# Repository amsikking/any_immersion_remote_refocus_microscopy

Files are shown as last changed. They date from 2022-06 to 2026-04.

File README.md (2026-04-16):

# Any immersion remote refocus (AIRR) microscopy



A scientific publication that describes a new approach for any immersion remote refocus (AIRR) microscopy. This repository 
hosts everything you need to reproduce our results. Read the publication here:
https://amsikking.github.io/any_immersion_remote_refocus_microscopy (hosted via Alfred Millett-Sikking's personal GitHub account).

This repository is intended to hold a (mostly) self-contained scientific publication. It contains:

* HTML, javascript, CSS, and small images (`index.html`, `appendix.html`, and the `javascript`, `stylesheets`, and `images` directories)
* A (limited) PDF version of the publication; note that this does not include animated/interactive figures.
* Code which produces figures (in the `figures` directory). You can run and modify this code to verify and explore our results.

<a rel="license" href="http://creativecommons.org/licenses/by/4.0/">
  </a>
  <br />This work is licensed under a 
  <a rel="license" href="http://creativecommons.org/licenses/by/4.0/">Creative Commons Attribution 4.0 International License</a>.

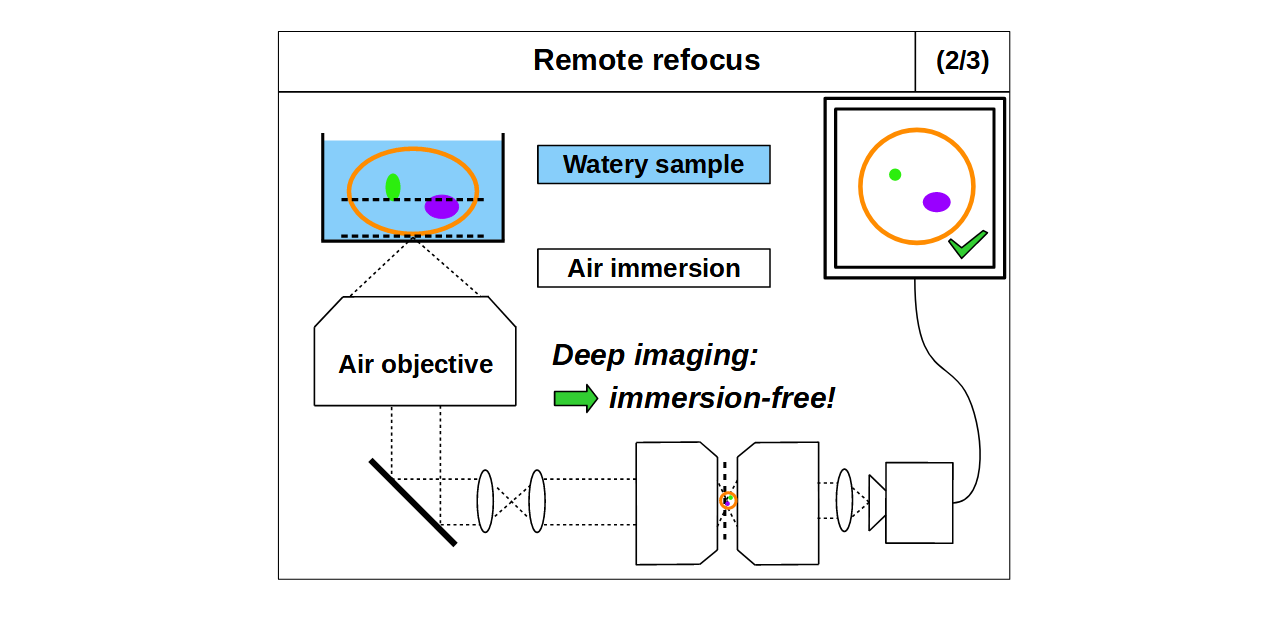
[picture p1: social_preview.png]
social_preivew


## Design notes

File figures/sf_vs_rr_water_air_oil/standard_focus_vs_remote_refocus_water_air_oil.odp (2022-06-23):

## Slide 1

Standard focus

(1/3)

Watery sample

Water immersion

Deep imaging:

needs matched refractive index

Water objective

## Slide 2

Standard focus

(1/3)

Watery sample

Water immersion

Deep imaging:

needs matched refractive index

Water objective

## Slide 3

Standard focus

(1/3)

Watery sample

Water immersion

Deep imaging:

needs matched refractive index

Water objective

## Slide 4

Standard focus

(1/3)

Watery sample

Water immersion

Water objective

Deep imaging:

needs matched refractive index

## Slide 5

Standard focus

(1/3)

Watery sample

Watery sample

Water immersion

Water immersion

Water objective

Deep imaging:

needs matched refractive index

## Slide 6

Standard focus

(1/3)

Watery sample

Water immersion

Water objective

Deep imaging:

needs matched refractive index

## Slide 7

Standard focus

(1/3)

Watery sample

Water immersion

Water objective

Deep imaging:

needs matched refractive index

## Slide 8

Standard focus

(1/3)

Watery sample

Water immersion

Water objective

Deep imaging:

needs matched refractive index

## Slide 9

Standard focus

(1/3)

Watery sample

Water immersion

Water objective

Deep imaging:

needs matched refractive index

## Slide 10

Standard focus

(1/3)

Watery sample

Water immersion

Water objective

Deep imaging:

needs matched refractive index

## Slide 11

Standard focus

(1/3)

Watery sample

Water immersion

Water objective

Deep imaging:

needs matched refractive index

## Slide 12

Standard focus

(1/3)

Watery sample

Water immersion

Water objective

Deep imaging:

needs matched refractive index

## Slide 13

Standard focus

(1/3)

Watery sample

Water immersion

Deep imaging:

needs matched refractive index

Water objective

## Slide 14

Standard focus

(1/3)

Watery sample

Water immersion

Deep imaging:

needs matched refractive index

Water objective

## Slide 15

Standard focus

(1/3)

Watery sample

Water immersion

Deep imaging:

needs matched refractive index

Water objective

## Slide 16

Standard focus

(2/3)

Watery sample

Air immersion

Deep imaging:

disrupted by spherical aberration

Air objective

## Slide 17

Standard focus

(2/3)

Watery sample

Air immersion

Deep imaging:

disrupted by spherical aberration

Air objective

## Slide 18

Standard focus

(2/3)

Watery sample

Air immersion

Deep imaging:

disrupted by spherical aberration

Air objective

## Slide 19

Standard focus

(2/3)

Watery sample

Air immersion

Air objective

Deep imaging:

disrupted by spherical aberration

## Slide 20

Standard focus

(2/3)

Watery sample

Air immersion

Air objective

Deep imaging:

disrupted by spherical aberration

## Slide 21

Standard focus

(2/3)

Watery sample

Air immersion

Air objective

Deep imaging:

disrupted by spherical aberration

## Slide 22

Standard focus

(2/3)

Watery sample

Air immersion

Air objective

Deep imaging:

disrupted by spherical aberration

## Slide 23

Standard focus

(2/3)

Watery sample

Air immersion

Air objective

Deep imaging:

disrupted by spherical aberration

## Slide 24

Standard focus

(2/3)

Watery sample

Air immersion

Air objective

Deep imaging:

disrupted by spherical aberration

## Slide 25

Standard focus

(2/3)

Watery sample

Air immersion

Air objective

Deep imaging:

disrupted by spherical aberration

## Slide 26

Standard focus

(2/3)

Watery sample

Air immersion

Air objective

Deep imaging:

disrupted by spherical aberration

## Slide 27

Standard focus

(2/3)

Watery sample

Air immersion

Air objective

Deep imaging:

disrupted by spherical aberration

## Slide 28

Standard focus

(2/3)

Watery sample

Air immersion

Deep imaging:

disrupted by spherical aberration

Air objective

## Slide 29

Standard focus

(2/3)

Watery sample

Air immersion

Deep imaging:

disrupted by spherical aberration

Air objective

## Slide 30

Standard focus

(2/3)

Watery sample

Air immersion

Deep imaging:

disrupted by spherical aberration

Air objective

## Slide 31

Standard focus

(3/3)

Watery sample

Oil immersion

Deep imaging:

disrupted by spherical aberration

Oil objective

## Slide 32

Standard focus

(3/3)

Watery sample

Oil immersion

Deep imaging:

disrupted by spherical aberration

Oil objective

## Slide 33

Standard focus

(3/3)

Watery sample

Oil immersion

Deep imaging:

disrupted by spherical aberration

Oil objective

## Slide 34

Standard focus

(3/3)

Watery sample

Oil immersion

Oil objective

Deep imaging:

disrupted by spherical aberration

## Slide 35

Standard focus

(3/3)

Watery sample

Oil immersion

Oil objective

Deep imaging:

disrupted by spherical aberration

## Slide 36

Standard focus

(3/3)

Watery sample

Oil immersion

Oil objective

Deep imaging:

disrupted by spherical aberration

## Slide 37

Standard focus

(3/3)

Watery sample

Oil immersion

Oil objective

Deep imaging:

disrupted by spherical aberration

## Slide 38

Standard focus

(3/3)

Watery sample

Oil immersion

Oil objective

Deep imaging:

disrupted by spherical aberration

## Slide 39

Standard focus

(3/3)

Watery sample

Oil immersion

Oil objective

Deep imaging:

disrupted by spherical aberration

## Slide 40

Standard focus

(3/3)

Watery sample

Oil immersion

Oil objective

Deep imaging:

disrupted by spherical aberration

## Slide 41

Standard focus

(3/3)

Watery sample

Oil immersion

Oil objective

Deep imaging:

disrupted by spherical aberration

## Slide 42

Standard focus

(3/3)

Watery sample

Oil immersion

Oil objective

Deep imaging:

disrupted by spherical aberration

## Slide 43

Standard focus

(3/3)

Watery sample

Oil immersion

Deep imaging:

disrupted by spherical aberration

Oil objective

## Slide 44

Standard focus

(3/3)

Watery sample

Oil immersion

Deep imaging:

disrupted by spherical aberration

Oil objective

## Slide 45

Standard focus

(3/3)

Watery sample

Oil immersion

Deep imaging:

disrupted by spherical aberration

Oil objective

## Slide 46

Remote refocus

(1/3)

Watery sample

Water immersion

Deep imaging:

extra range!

Water objective

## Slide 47

Remote refocus

(1/3)

Watery sample

Water immersion

Deep imaging:

extra range!

Water objective

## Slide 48

Remote refocus

(1/3)

Watery sample

Water immersion

Deep imaging:

extra range!

Water objective

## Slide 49

Remote refocus

(1/3)

Watery sample

Water immersion

Deep imaging:

extra range!

Water objective

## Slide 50

Remote refocus

(1/3)

Watery sample

Water immersion

Deep imaging:

extra range!

Water objective

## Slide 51

Remote refocus

(1/3)

Watery sample

Water immersion

Deep imaging:

extra range!

Water objective

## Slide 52

Remote refocus

(1/3)

Watery sample

Water immersion

Deep imaging:

extra range!

Water objective

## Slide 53

Remote refocus

(1/3)

Watery sample

Water immersion

Deep imaging:

extra range!

Water objective

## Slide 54

Remote refocus

(1/3)

Watery sample

Water immersion

Deep imaging:

extra range!

Water objective

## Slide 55

Remote refocus

(1/3)

Watery sample

Water immersion

Deep imaging:

extra range!

Water objective

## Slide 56

Remote refocus

(1/3)

Watery sample

Water immersion

Deep imaging:

extra range!

Water objective

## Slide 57

Remote refocus

(1/3)

Watery sample

Water immersion

Deep imaging:

extra range!

Water objective

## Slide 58

Remote refocus

(1/3)

Watery sample

Water immersion

Deep imaging:

extra range!

Water objective

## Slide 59

Remote refocus

(1/3)

Watery sample

Water immersion

Deep imaging:

extra range!

Water objective

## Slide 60

Remote refocus

(1/3)

Watery sample

Water immersion

Deep imaging:

extra range!

Water objective

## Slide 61

Remote refocus

(2/3)

Watery sample

Air immersion

Deep imaging:

immersion-free!

Air objective

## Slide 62

Remote refocus

(2/3)

Watery sample

Air immersion

Deep imaging:

immersion-free!

Air objective

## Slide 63

Remote refocus

(2/3)

Watery sample

Air immersion

Deep imaging:

immersion-free!

Air objective

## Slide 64

Remote refocus

(2/3)

Watery sample

Air immersion

Deep imaging:

immersion-free!

Air objective

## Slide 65

Remote refocus

(2/3)

Watery sample

Air immersion

Deep imaging:

immersion-free!

Air objective

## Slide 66

Remote refocus

(2/3)

Watery sample

Air immersion

Deep imaging:

immersion-free!

Air objective

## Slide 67

Remote refocus

(2/3)

Watery sample

Air immersion

Deep imaging:

immersion-free!

Air objective

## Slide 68

Remote refocus

(2/3)

Watery sample

Air immersion

Deep imaging:

immersion-free!

Air objective

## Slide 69

Remote refocus

(2/3)

Watery sample

Air immersion

Deep imaging:

immersion-free!

Air objective

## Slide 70

Remote refocus

(2/3)

Watery sample

Air immersion

Deep imaging:

immersion-free!

Air objective

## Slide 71

Remote refocus

(2/3)

Watery sample

Air immersion

Deep imaging:

immersion-free!

Air objective

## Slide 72

Remote refocus

(2/3)

Watery sample

Air immersion

Deep imaging:

immersion-free!

Air objective

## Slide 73

Remote refocus

(2/3)

Watery sample

Air immersion

Deep imaging:

immersion-free!

Air objective

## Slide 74

Remote refocus

(2/3)

Watery sample

Air immersion

Deep imaging:

immersion-free!

Air objective

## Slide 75

Remote refocus

(2/3)

Watery sample

Air immersion

Deep imaging:

immersion-free!

Air objective

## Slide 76

Remote refocus

(3/3)

Watery sample

Oil immersion

Deep imaging:

highest NA!

Oil objective

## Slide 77

Remote refocus

(3/3)

Watery sample

Oil immersion

Deep imaging:

highest NA!

Oil objective

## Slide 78

Remote refocus

(3/3)

Watery sample

Oil immersion

Deep imaging:

highest NA!

Oil objective

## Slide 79

Remote refocus

(3/3)

Watery sample

Oil immersion

Deep imaging:

highest NA!

Oil objective

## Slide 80

Remote refocus

(3/3)

Watery sample

Oil immersion

Deep imaging:

highest NA!

Oil objective

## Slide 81

Remote refocus

(3/3)

Watery sample

Oil immersion

Deep imaging:

highest NA!

Oil objective

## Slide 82

Remote refocus

(3/3)

Watery sample

Oil immersion

Deep imaging:

highest NA!

Oil objective

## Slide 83

Remote refocus

(3/3)

Watery sample

Oil immersion

Deep imaging:

highest NA!

Oil objective

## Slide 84

Remote refocus

(3/3)

Watery sample

Oil immersion

Deep imaging:

highest NA!

Oil objective

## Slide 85

Remote refocus

(3/3)

Watery sample

Oil immersion

Deep imaging:

highest NA!

Oil objective

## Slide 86

Remote refocus

(3/3)

Watery sample

Oil immersion

Deep imaging:

highest NA!

Oil objective

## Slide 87

Remote refocus

(3/3)

Watery sample

Oil immersion

Deep imaging:

highest NA!

Oil objective

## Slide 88

Remote refocus

(3/3)

Watery sample

Oil immersion

Deep imaging:

highest NA!

Oil objective

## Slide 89

Remote refocus

(3/3)

Watery sample

Oil immersion

Deep imaging:

highest NA!

Oil objective

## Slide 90

Remote refocus

(3/3)

Watery sample

Oil immersion

Deep imaging:

highest NA!

Oil objective

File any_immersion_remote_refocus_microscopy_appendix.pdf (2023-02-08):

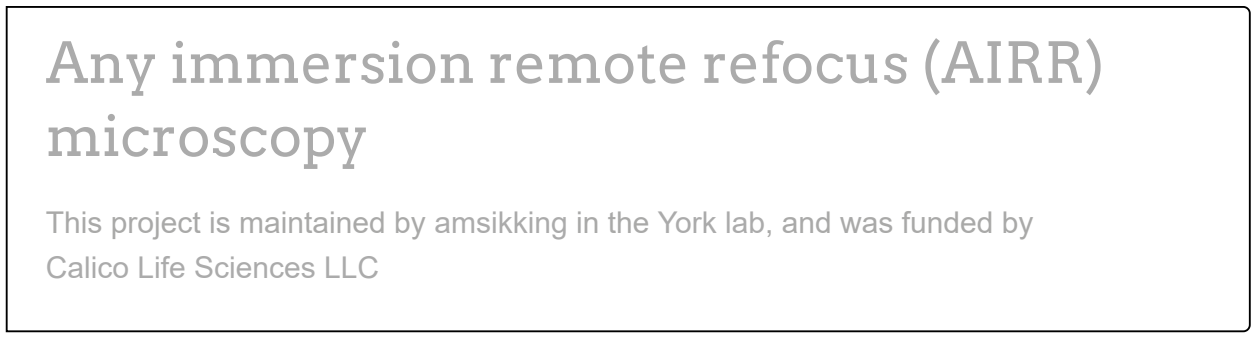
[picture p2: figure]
Any immersion remote refocus (AIRR) microscopy; Calico Life Sciences LLC

This project is maintained by amsikking (https://amsikking.github.io/) in the York lab, (https://andrewgyork.github.io/) and was funded by

# Appendix

Note that this is a limited PDF or print version; animated and interactive figures are disabled. For the full version of this article, please visit one of the following links: https://amsikking.github.io/any_immersion_remote_refocus_microscop y (https://amsikking.github.io/any_immersion_remote_refocus_microscopy)

# Any immersion remote refocus (AIRR) microscopy

Back to the main text

## Theory

Here we present the equations used in the main article.

Numerical aperture and resolution

The numerical aperture (NA) is defined as:

where | is the refractive index (RI) of the immersion medium and | is the collection half-angle of the objective.
In the case of a planar RI boundary like a coverslip the NA is conserved via Snell's law:
where | is the RI of the sample and | is the collection half-angle in sample space. According to the Rayleigh
criteria the smallest resolvable feature size | is then:
NA = ni sin θi | (a1)
ni | θi
ns sin θs = ni sin θi | (a2)
ns | θs

rmin where is the wavelength of the collected light [Pawley 2006]. (https://doi.org/10.1007/978-0-387-45524-2)

Focal length, field of view and pixels

The objective lens focal length is found with:

where | is the tube lens focal length (200mm for Nikon) and | is the magnification of the objective. The
sample space field of view (FOV) is then assumed to be:

where FN is the field number according to the manufacturer (20mm assumed for Nikon). When choosing an objective it can be useful to estimate the number of Nyquist pixels the lens can deliver across the FOV using:

Note: this can be useful for choosing a camera and also serves as a measure of the quality of the objective, where more pixels usually indicates a more sophisticated lens design (similar in concept to etendue).

Standard focus depth

From Sheppard 1991, (https://www.researchgate.net/publication/235927740_Effects_of_aberrating_layers_and_tube_length_on_con_focal_imaging_properties) equation 18 proposes that in a medium of refractive index , the maximum acceptable wavefront aberration (Rayleigh criterion) will not be exceeded if the thickness of a slab of dielectric and
refractive index | meets the following condition:
where is the collection half-angle in the | space (i.e. the immersion). Originally evaluated for a phase error
of | , equation | gives negative values for | . If we allow | and a phase error of | then
we can rewrite | in a slightly more convenient format to give the maximum depth of standard focus | :

Remote refocus depth

From Botcherby 2007, (https://doi.org/10.1016/j.optcom.2007.10.007) equation 23 proposes that the Strehl ratio of a remote refocus can be modeled by:

rmin = 0.61 | (a3)

λ
NA

λ

f

f = | (a4)

fTL
M
fTL | M
FOV = | (a5)

FN
M

Npx

Npx = 2 | (a6)

FOV

rmin

n1

t

n2

t ≤ | (a7)

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
2 − n

2
1

)sin

4
(α/2)
α | n1
π/2 | (a7) | n1 > n2 | n1 > n2 | ±π/2
| (a7) | | | zsf_max

zsf_max =

∣
∣
∣

∣
∣
∣

(a8)

λ

2 sin

4
(θi/2)

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
s − n

2
i

)

S

where is the refractive index of the sample, | is the wavenumber, is the axial distance from the
traditional focal plane, is the focal length and is the collection half-angle of the objective. If we set
(the traditional diffraction limit) and rearrange we can estimate the maximum remote refocus depth | :
Note: the substitution | is subtle. In Botcherby 2007 (https://doi.org/10.1016/j.optcom.2007.10.007) at the critical substitution of equation 8 (
) the paper reads "In this expression is the semi-aperture acceptance angle of the lens" so
one could assume | . However the substitution is in reference to coordinates in object space.

Combined depth

For a microscope with remote refocus optics (e.g. Figure 2) we can now estimate the maximum focus depth in the sample as the sum of the standard and remote depths:

Note: the approximately equals sign. The standard focus and remote refocus depths use different definitions for the diffraction limit, and are approximate models that ignore higher order aberrations. There is also no consideration given to field effects, chromatic aberrations or design and manufacturing imperfections that can be expected in real objective lenses.

## Objective selection

In a SOLS microscope [Millett-Sikking 2019], (https://doi.org/10.5281/zenodo.3244420) as the half angle in the sample | decreases, the tilt of the last
microscope | increases according to:

Currently the AMS-AGY v2.0 objective [Yang 2022] (https://doi.org/10.1038/s41592-022-01417-2) has the most extreme tilt range of any SOLS compatible
objective, with maximum tilt of 55 degrees. So combining | , | and | the minimum acceptable
sample space NA is:

After applying the lower bound on NA of 0.76, the 'best' objectives for the standard immersions were selected in the following 2 categories:

Nikon objectives, highest NA:

Part # | M | NA | Imm. | WD (μm) | FOV (μm) | rmin (μm) | N_px
S = 1 − | (a9)

4n

2k

2z

4
(3 + 16 cos α + cos 2α)sin

8
(α/2)

75f

2(3 + 8 cos α + cos 2α)

n | k = 2π/λ | z
f | α | S = 0.8
| | zrr_max
zrr_max = ± | √4 | (a10)
1

2 sin

2
(θs/2)

15λ

2f

2(3 + 8 cos θs + cos 2θs)

π

2n

2
s(3 + 16 cos θs + cos 2θs)

α = θs

sin θ = ρ sin α | α

α = θi

zmax

zmax ≈ zsf_max + |zrr_max| | (a11)

θs

θtilt

θtilt = 90 − θs | (deg) | (a13)
(a1) (a2) | (a13)
NA ≥ 1.33 sin(90 − 55) = 0.76 | (a14)

MRD70470 | 40x | 0.95 | air | 210 | 500 | 0.342 | 2927
MRY10060 | 60x | 1.27 | water | 180 | 333 | 0.256 | 2608
MRD73950 | 100x | 1.35 | silicone | 310 | 200 | 0.240 | 1663
MRD71970 | 100x | 1.45 | oil | 130 | 200 | 0.224 | 1787

Nikon objectives, most pixels:

Part # | M | NA | Imm. | WD (μm) | FOV (μm) | rmin (μm) | N_px
MRD70270 | 20x | 0.80 | air | 800 | 1000 | 0.406 | 4930
MRD77200 | 20x | 0.95 | water | 990 | 1000 | 0.342 | 5854
MRD73250 | 25x | 1.05 | silicone | 550 | 800 | 0.309 | 5176
MRH01401 | 40x | 1.30 | oil | 240 | 500 | 0.250 | 4005

Note: Speciality objectives in the categories of TIRF and Multi-photon may not perform optimally for RR and were avoided.

## Zoom lens

In our previous RR designs we used static lenses to adjust the magnification between the sample and the remote space according to equation 2 [Millett-Sikking 2018, (https://doi.org/10.5281/zenodo.1146083) Millett-Sikking 2019]. (https://doi.org/10.5281/zenodo.3244420) Specifically we chose to modify the second tube lens in the optical train, often referred to as 'tube lens 2' or TL2. The TL2 location is convenient, as it leaves the first objective and tube lens pair in their traditional (stock) configuration, and allows the addition of a unity magnification scanning system. Here we take the same approach, and optimize our zoom optics at the TL2 location, specifying some of the upstream and downstream optics in order to produce a concrete design.

Specifications

To produce a zoom lens with stock parts we narrow the optical requirement to a specific RR system. We assume a standard microscope at 40x magnification since this offers many attractive primary objective options (air, water, silicone and oil immersion at high NA from various manufacturers). We then assume a 5mm focal length air lens for the second RR objective (often referred to as 'objective 2' or O2). For example the Nikon 40x0.95 air lens (9.5mm back focal plane diameter) is a good high NA option, with a high enough collection cone (~72deg) and pixel count (~2927) for most RR designs. We target a RR magnification that covers the full biological RI range (1.33-1.51) by tuning the focal length of TL2 in the range 150-132.5mm (i.e. 30-26.5x for microscope 2). Finally we assume a standard sCMOS field of view (~13.5mm width) and add the additional constraints of needing a constant track length and telecentric image.

Design

Using the above specifications, we adopt a simple 'positive-negative-positive' (PNP) zoom design and cycle through readily available stock parts. After some iteration we settle on a series of Edmund Optics achromats that satisfy our optical requirements, whilst also being mechanically compatible and inexpensive (see the mechanics section for parts). Our constraint of only using stock lenses forces a 5 achromat solution (Figure A2), where a 3 achromat custom design would suffice. We note that a 'standard' tube lens typically has 2 achromats, so a 3 lens solution would only add 1 achromat to the optical train (a minimal drawback for the system). However, we consider the small penalty on transmission efficiency (~1.5%) from the 2 additional achromats in the design we present to be a good trade for avoiding bespoke glass.

Performance

In Figure A1 we see the spot diagrams as a function of field (center to edge) and configuration (min to max focal length) across the visible spectrum (450-700nm). We can see that the system is mostly diffraction limited throughout the matrix, with some marginal degradation at the edge of the field for the shorter focal lengths (higher RR magnifications). In the interactive Figure A2 we show detailed views of the performance at the extremes of the range with configurations 1 and 8 (i.e. magnifications of 1.33 and 1.51). See zoom_lens.zip for more details (including Zemax files).

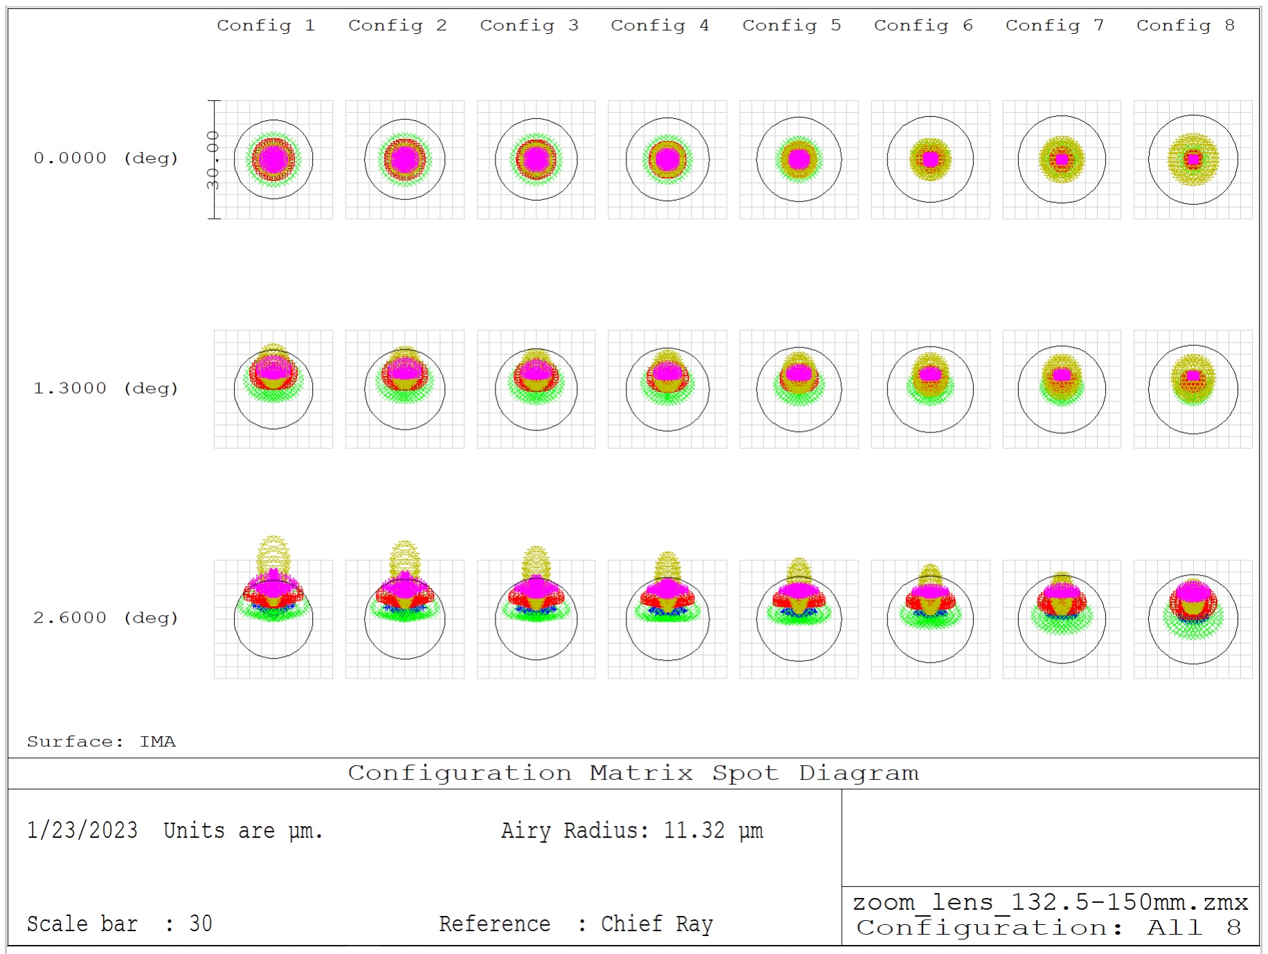
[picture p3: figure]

Figure A1: Multi-configuration spot diagram. This screen shot from Zemax shows the spot diagrams as a function of field (0, 1.3 and 2.6deg) and configurations (1-8) across the visible spectrum (450-700nm). Here the configurations 1 to 8 correspond to target focal lengths of 132.5mm to 150mm in steps of 2.5mm. Spots that appear within the Airy diameter (black ring) can be considered diffraction limited.

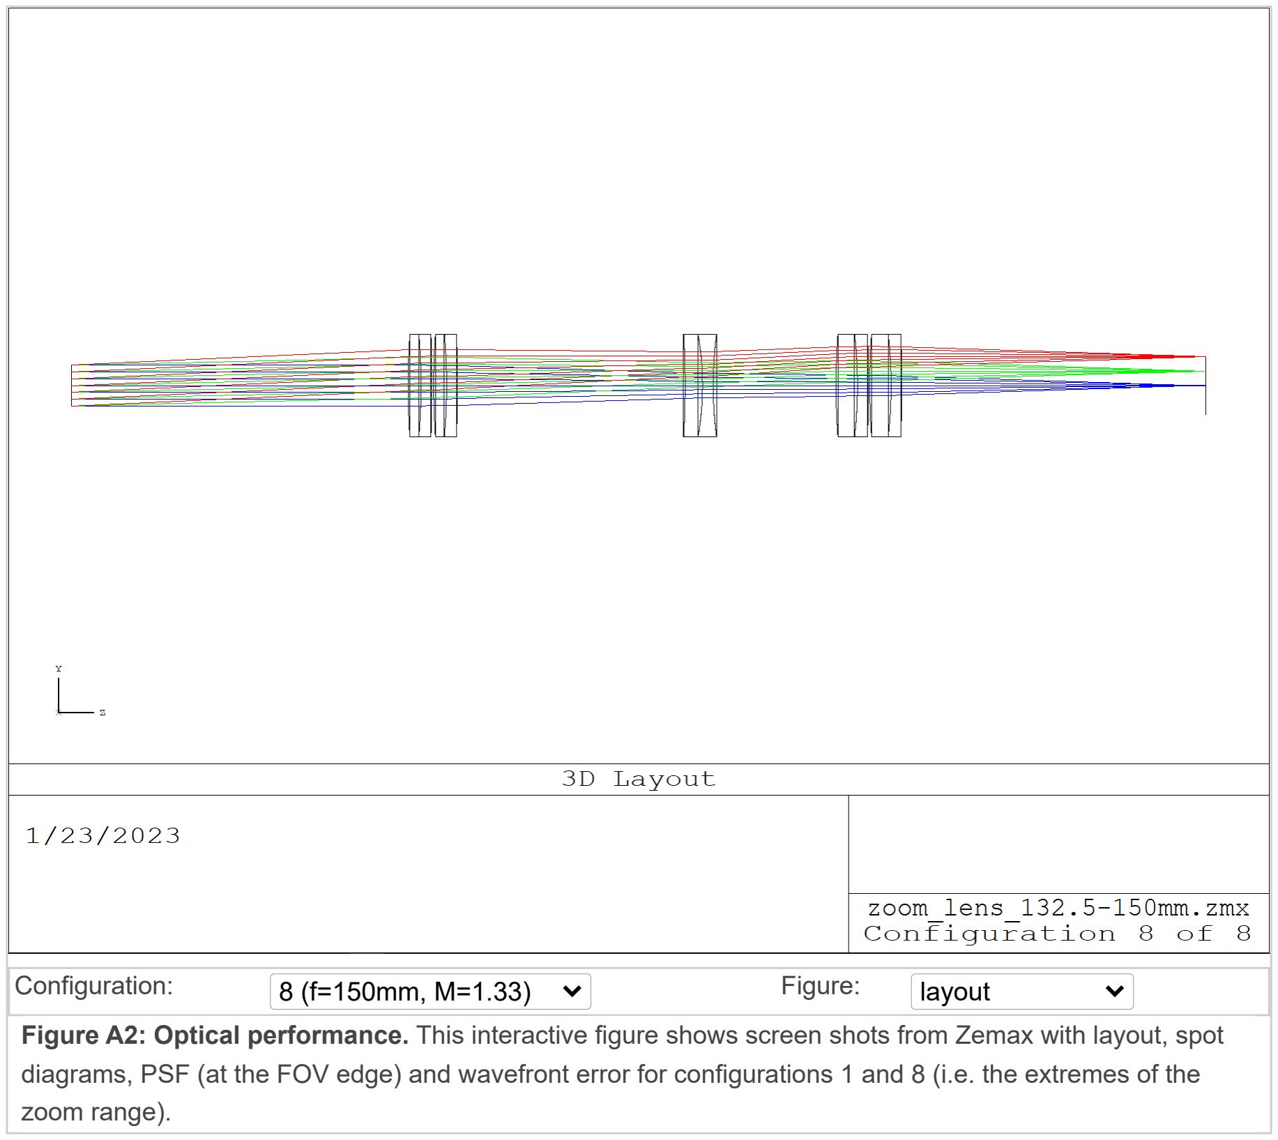
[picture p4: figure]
Configuration:; Figure:; layout

| Figure A2: Optical performance. This interactive figure shows screen shots from Zemax with layout, spot diagrams, PSF (at the FOV edge) and wavefront error for configurations 1 and 8 (i.e. the extremes of the zoom range).

Motion

Part of the design challenge in a zoom system is accommodating the motion of elements (or groups of elements). Here we adopt relatively large motions of all 3 lens groups from the PNP design. This has the drawback of being slower than small motions, but the benefit of loosening the opto-mechanical tolerances of the system, thereby allowing us to use stock optics and mechanics. In Figure A3 we see how we need to move the lens groups from the 'zero position' with a focal length of 132.5mm to the 'limit position' with a focal length of 150mm. The negative lens (center element in the design) moves the most by up to ~66mm, while the positive groups near the objective and the image move by up to ~18mm and ~42mm respectively.

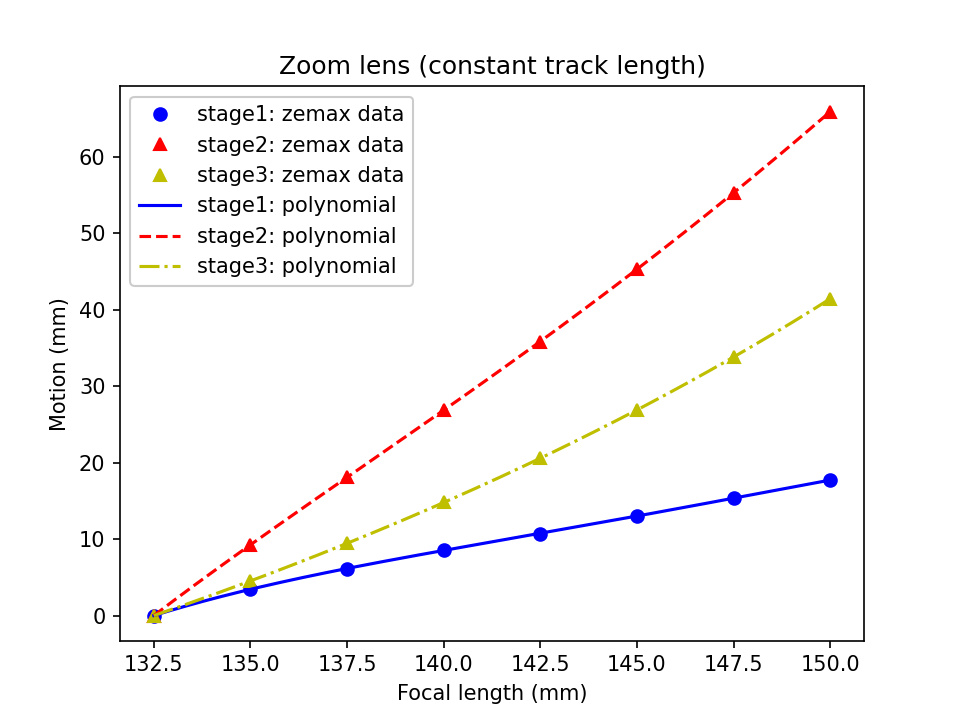
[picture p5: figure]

Figure A3: Zoom lens motion. This plot shows how the lens groups should move to produce a given focal length for the zoom lens. The 'stage1' curve is the required motion for the positive lens group near the objective (O2), the 'stage2' curve is for the negative central element and the 'stage3' curve is for the positive lens group near the image plane.

Below we provide the 'motion functions' that convert a requested focal length to a required movement of each lens or lens group (for driving linear stages or equivalent mechanics). Here's an example for a focal length of 140mm:

# Zoom_lens_132.5-150mm_motion.ods trendline polynomials # Data from Zemax

def focal_length_to_lens_motion(f_mm, verbose=True):
stage1_mm | = | (- | 0.000103278288*f_mm**4
| | + | 0.059929457484*f_mm**3
- 13.033982374525*f_mm**2
| | + | 1260.150733009060*f_mm
- 45717.573446038600)
stage2_mm | = | (- | 0.000083979119*f_mm**4
| | + | 0.049656589716*f_mm**3
- 10.961078884880*f_mm**2
| | + | 1074.586675413890*f_mm
- 39574.398463973600)

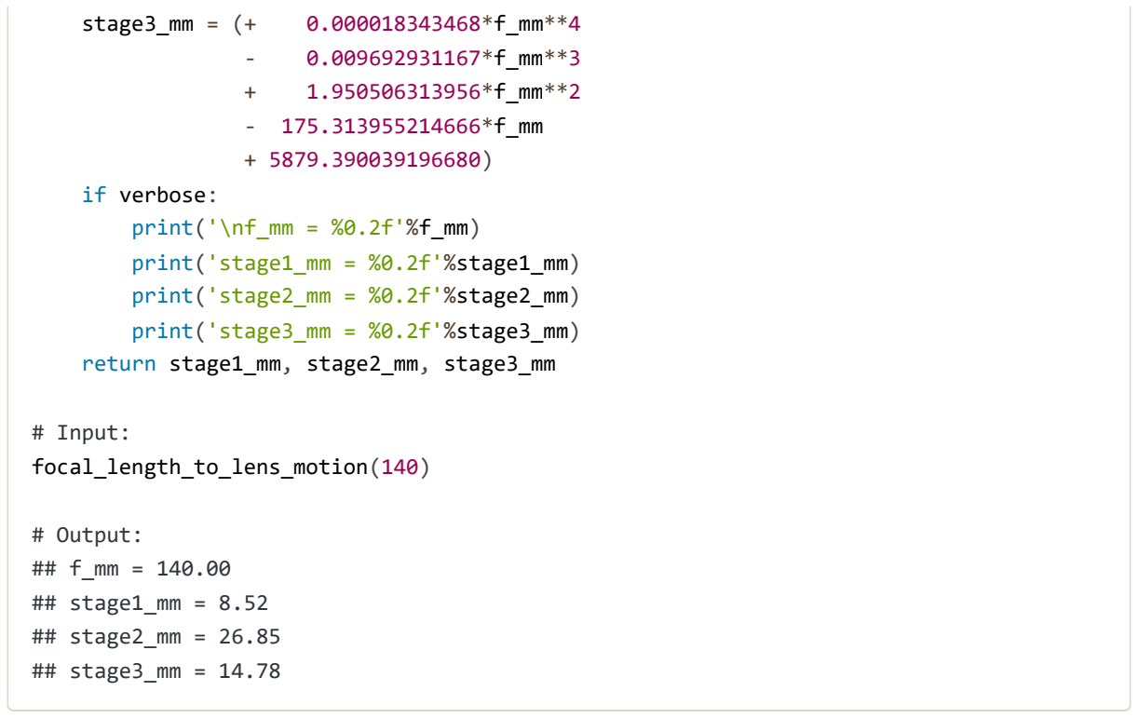
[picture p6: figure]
stage3_mm; if verbose: print('\nf_mm = %0.2f'%f_mm) print('stage1_mm = %0.2f'%stage1_mm) print('stage2_mm = %0.2f'%stage2_mm) print('stage3_mm = %0.2f'%stage3_mm) return stage1_mm, stage2_mm, stage3_mm; # Input: focal_length_to_lens_motion(140); # Output: ## f_mm = 140.00 ## stage1_mm = 8.52 ## stage2_mm = 26.85 ## stage3_mm = 14.78

Mechanics

Here we offer a relatively simple mechanical design (Figure A4), that utilizes some fast 50-100mm linear stages from Thorlabs (parts DDS050 and DDS100). However, any mechanical solution that achieves the required alignment of the lenses and relative motions is acceptable. The solution we present combines the zoom optics into a single large mount that can be aligned to an axis that is parallel to the optical table, and includes provision for an objective and a dichroic. The DDS stages have a max speed of 500mm/s so we can expect a responsive zoom experience for tuning the magnification to different sample types. See the included zoom_lens_132.5-150mm.pdf for a high quality reproduction of the 2D drawings, or 3D CAD in eDrawings, Solidworks or .STEP format.

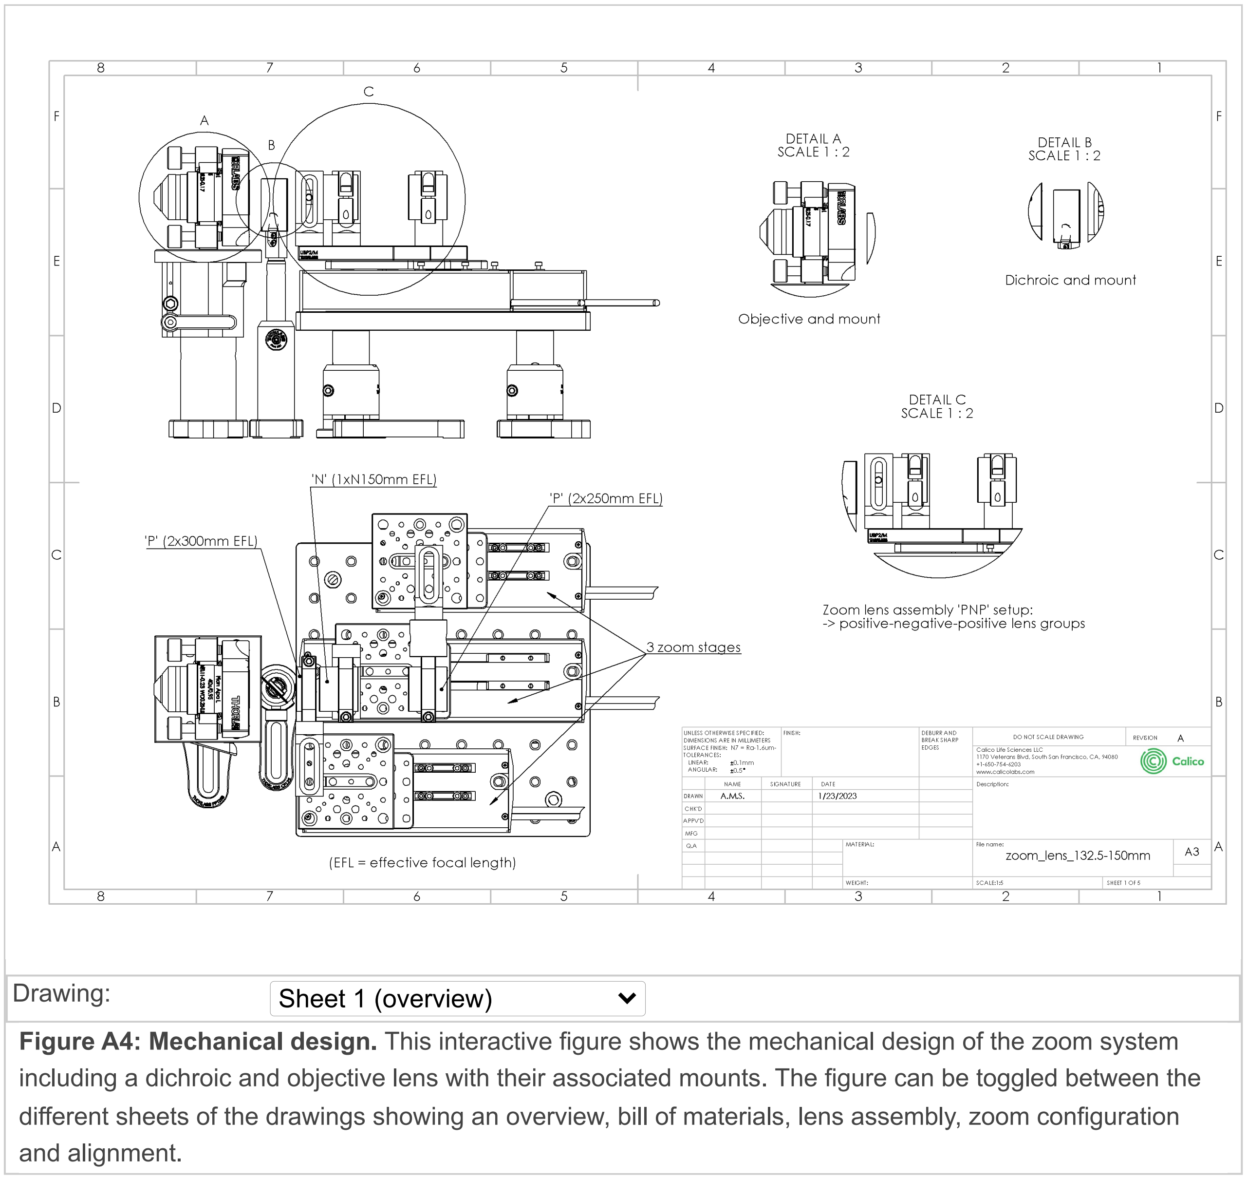
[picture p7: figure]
Drawing:; Sheet 1 (overview); and alignment.

Figure A4: Mechanical design. This interactive figure shows the mechanical design of the zoom system including a dichroic and objective lens with their associated mounts. The figure can be toggled between the different sheets of the drawings showing an overview, bill of materials, lens assembly, zoom configuration

Alignment

The alignment of the zoom lens can be tricky, but with patients and good practice it can be done. For an experienced builder a morning or afternoon should be enough time. Here are some pointers:

Setup a low power (~1mW) collimated laser beam with an adjustable diameter from ~1mm to ~10mm. A green laser beam like 532nm is preferred, since it has a central wavelength in the visible spectrum and appears bright to the human eye. Adjust the beam so it's horizontal to the optical table. Use the ~1mm beam for checking beam deviation and back reflections when aligning lenses to the laser beam. Use the ~10mm beam for checking the position of the focal planes.
From the fully assembled 'PNP' zoom lens, remove the positive (P) lens groups, leaving only the negative
(N) lens on the DDS100 motorized stage. Now iteratively adjust the 'XY' and 'tip/tilt' of the negative lens until the back reflections from the laser are centered on the ~1mm aperture. The back reflections should be symmetric over the full range of the zoom lens (~100mm here).

Using a separate mount, align the positive lens groups to the ~1mm laser beam and check the back reflections. Because the positive groups consist of 2 separate achromats in a tube, it's possible for them to be poorly set and not share the same optical axis. This will show in the back reflections where no combination of 'XY' and 'tip/tilt' adjustment gives a clean and symmetric reflection. In this case the lenses need to be 're-seated' in the lens tubes. Loosening the lens retaining ring and giving a gentle shake of the lens tube in a vertical position seems to work. Some repetition may be needed.
Now add the positive lens groups to the zoom lens assembly one at a time. For each lens group addition, repeat the iterative 'XY' and 'tip/tilt' alignment for that group (without changing the alignment of any other group), making sure the back reflection is clean over the full range of the zoom (~50mm here).

Control

Here's an example script for changing the focal length of the zoom lens across the full range (132.5-150mm). Before attempting to run this script, make sure the individual device adaptors for the DDS050 (https://github.com/amsikking/thorlabs_DDS050) and DDS100 (https://github.com/amsikking/thorlabs_DDS100) motorized stages are working, that the mechanical assembly is correct and the start positions of the stages are appropriate for the homing routine.

Testing

It's worth verifying the performance of the zoom lens before incorporating it into a system. According to the optical design, the 'Z' position of the front focal plane (FFP) and back focal plane (BFP) should be stable over the full range of the zoom. This can be tested in practice by observing a maximal 'speckle' pattern from some aluminum foil or a glass diffuser placed in the focus of the zoom lens (Figure A5). With this test we found the FFP and BFP tolerance to be better than +-100μm (see script and data here).

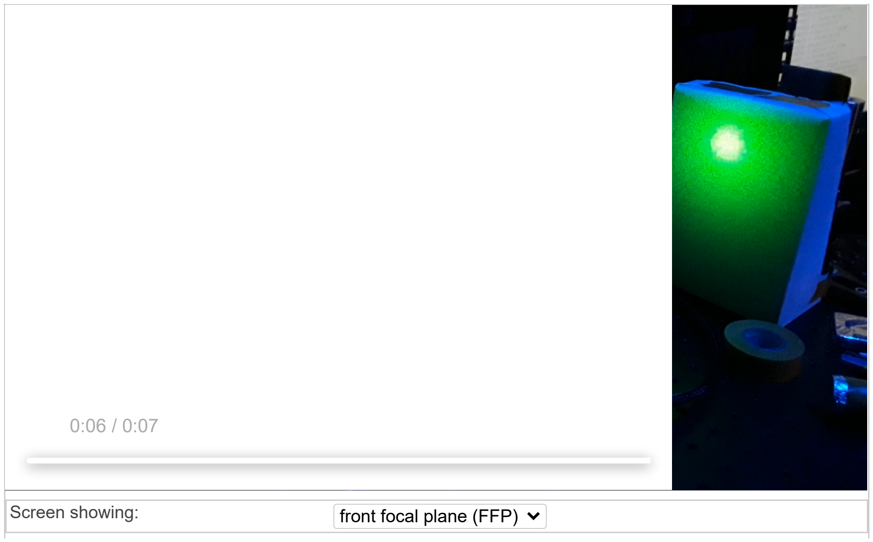
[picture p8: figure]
Screen showing:; front focal plane (FFP)

Figure A5: Speckle testing. This interactive figure shows the maximal speckle pattern from the focus of the zoom lens on a Thorlabs DG10-1500-MD glass diffuser as it cycles through the 8 Zemax configurations in the range 132.5-150mm. A collimated 532nm laser with a ~10mm diameter was used as the input beam. The figure can be toggled between the front focal plane (FFP) and back focal plane (BFP) orientations.

Alternatively the focused laser spot from the ~10mm diameter beam can be imaged directly with a camera to confirm it's XY and Z location as the zoom lens is adjusted over the full range (Figure A6). Here we performed this test by sweeping a small camera through the focus for each of the 8 Zemax configurations (see acquisition script). With this setup we also found the maximum FFP and BFP deviations to be less than +-100μm, and XY deviations in spot position to be less than ~40μm. Better results may be possible with more thorough alignment. Download FFP_data.zip and BFP_data.zip to see the data and run the scripts that estimate the focus position.

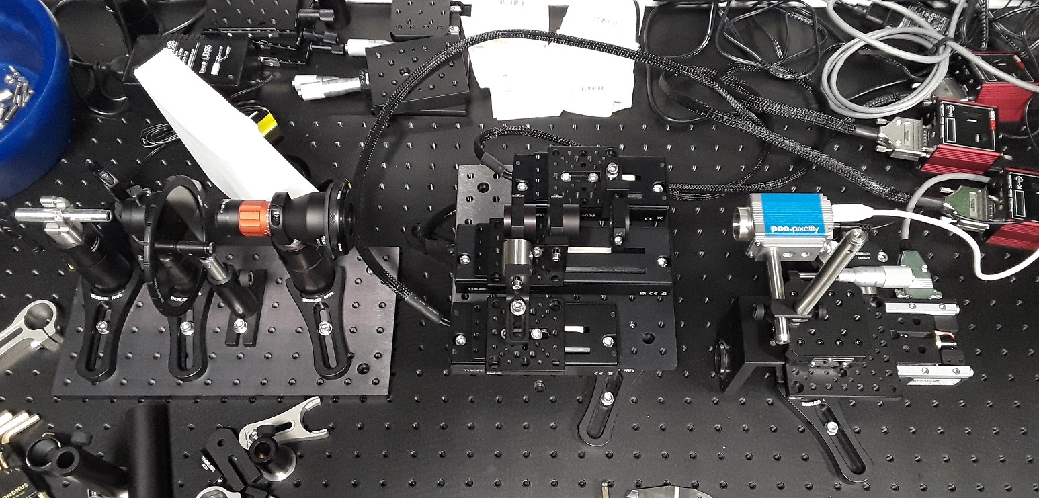
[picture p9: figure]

Figure A6: Camera testing. A photo of the camera based testing for the zoom lens. For each of the 8 Zemax configurations the camera was moved axially through the focus of the beam using a motorized stage. Images of the beam were captured at 25μm intervals.

If we assume a 40x magnification for the base microscope then a 40μm XY deviation in the image plane corresponds to a ~1μm XY shift in the sample (40μm/40), and a 100μm Z deviation in the focal plane to a ~60nm Z shift in the sample (100μm/40^2). Note that the maximum numerical aperture for the zoom lens is ~0.38 (5/132.5), and so the +-100μm result is within the traditional depth of field of ~370μm (0.532/0.38^2).

## Large FOV SOLS

Current prototype

On the road to building an 'any immersion' large FOV SOLS microscope we opted to build a 'static' configuration (i.e. no zoom lens) to show the potential of the new approach. The system was built to accommodate primary objectives with a 5mm effective focal length (i.e. the Nikon 40x family) with a remote refocus tuned for watery samples (i.e. a sample RI of 1.33). The transition from air to water immersion is one of the most extreme examples of an RI mismatch and so the Nikon 40x0.95 air and 40x1.15 water objectives were chosen as options for the primary objective. The last microscope (often referred to as microscope 3 in a SOLS design) was tilted to 50deg to accommodate the NA of both the air and water objectives. A simple cylindrical lens light-sheet excitation path was assembled, and combined with the following emission path optics:

Item | Supplier | Part | Description
S | Biologist | Sample | preferred refractive index: 1.33
O1 | Nikon | MRD77410 or MRD00405 | CFI Apo LWD Lambda S 40XC WI (NA=1.15) or CFI Plan Apo Lambda 40XC (NA=0.95)
TL1 | Nikon | MXA22018 | Tube lens, EFL=200 mm
SL1 | Thorlabs | TTL100-A | Scan lens, EFL=100 mm
G1 | Thorlabs | GVS211/M | 1D Galvo system, ∅10 mm, E02 coated
SL2 | Thorlabs | TTL100-A | Scan lens, EFL=100 mm
TL2 | Thorlabs | AMS custom | Tube lens, EFL=300 mm
D | Chroma | ZT405/488/561/640rpcv2 | Quad band dichroic
O2 | Nikon | MRD00205 | CFI Plan Apo Lambda 20XC (NA 0.75)
O2* | Carolina | 633037 | Cover Glasses, Circles, 25 mm, Thickness 0.13-0.17 mm
O3 | ASI | AMS-AGY v2.0 | Special glass tipped objective (a.k.a. KingSnout)
E | Chroma | ZET405/488/561/640m | Quad emission filter, ∅25 mm mounted
TL3 | Thorlabs | TTL200MP | Tube lens, EFL=200 mm
C | PCO | edge 4.2 cl | sCMOS camera, 2048x2048 px, 6.5μm pitch

Data

The Python scripts that were used to run the microscope and process the data are included in the 'data' folder (download full repository). (https://github.com/amsikking/any_immersion_remote_refocus_microscopy/zipball/master) The microscope was aligned on a best effort basis, with an overexpanded Gaussian beam for the light-sheet input (wasteful but gave uniform illumination). The light-sheet was generated with a 1mm slit aperture just before the cylindrical lens which was mapped onto the O2 back focal plane with a 1:1 relay (so about 0.66mm at the O1 BFP in this configuration). The PSF data was processed with the same method as here (https://github.com/amsikking/SOLS_psf_data) (which includes sample data). To avoid bloat the raw data (~500GB) is not included here so the publication can be readily stored and circulated offline.

Improved configuration

Some attractive upgrades to the current prototype include:

Adding the zoom lens to allow continuous tuning of the remote refocus volume to the sample RI (which we expect to keep the light-sheet in better alignment).
Swapping O2 from the Nikon 20x0.75 air objective to the 40x0.95 air objective. This gives improved collection from higher NA primary objectives, and the 40x has the correct effective focal length (5mm) to pair with the zoom assembly.
Using a high quality coverslip at O2. ASI (https://www.asiimaging.com/) currently offers the Nikon 40x0.95 air objective with a high quality (AR coated) coverslip glued to the front.
Adjusting the focal length of tube lens 3 for a good compromise on the Nyquist pixel size (something like a 250mm EFL).

## References

1. [Pawley 2006] (https://doi.org/10.1007/978-0-387-45524-2) Handbook of Biological Confocal Microscopy, third edition; J. Pawley; Springer US, ISBN 978-0-387-25921-5, eBook ISBN 978-0-387-45524-2, (2006) https://doi.org/10.1007/978-0-387-45524-2
2. [Sheppard 1991] (https://www.researchgate.net/publication/235927740_Effects_of_aberrating_layers_and_tube_length_on_con_focal_imaging_properties) Effects of aberrating layers and tube length on con focal imaging properties; C. Sheppard and C. J. Cogswell; Optik, vol 87(1), p34-38, (1991) https://www.researchgate.net/publication/235927740_Effects_of_aberrating_layers_and_tube_length_on_con_focal_imaging_properties
3. [Botcherby 2007] (https://doi.org/10.1016/j.optcom.2007.10.007) An optical technique for remote focusing in microscopy; E.J. Botcherby, R. Juškaitis, M.J. Booth and T. Wilson; Optics Communications, vol 281(4), p880-887, (2007) https://doi.org/10.1016/j.optcom.2007.10.007
4. [Millett-Sikking 2019] (https://doi.org/10.5281/zenodo.3244420) High NA single-objective light-sheet; A. Millett-Sikking, K.M. Dean, R. Fiolka, A. Fardad, L. Whitehead and A.G. York; (2019) https://doi.org/10.5281/zenodo.3244420
5. [Yang 2022] (https://doi.org/10.1038/s41592-022-01417-2) DaXi—high-resolution, large imaging volume and multi-view single-objective light-sheet microscopy; B. Yang, M. Lange, A. Millett-Sikking, X. Zhao, J. Bragantini, S. VijayKumar, M. Kamb, R. Gómez-Sjöberg, A.C. Solak, W. Wang, H. Kobayashi, M.N. McCarroll, L.W. Whitehead, R.P. Fiolka, T.B. Kornberg, A.G. York and L.A. Royer; (2022) https://doi.org/10.1038/s41592-022-01417-2
6. [Millett-Sikking 2018] (https://doi.org/10.5281/zenodo.1146083) Remote refocus enables class-leading spatiotemporal resolution in 4D optical microscopy; A. Millett-Sikking, N.H. Thayer, A. Bohnert and A.G. York; (2018) https://doi.org/10.5281/zenodo.1146083

Hosted on
GitHub Pages (https://pages.github.com/)

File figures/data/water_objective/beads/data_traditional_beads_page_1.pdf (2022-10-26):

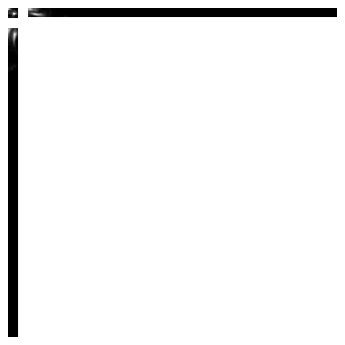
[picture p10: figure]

Bead 1 (Rejected)

Date : Mon Oct 17 13:27:37 PDT 2022
Origin : data_traditional.tif ( Nikon 40x1.15 water ) Frame size : 10 pixels

Coordinates : -133 um (x), 65.8 um (y), 1.38 um (z) Corresponding bead : Not found
Reason of rejection : R or C parameter off limits.

XY profile & fitting parameters :
(red : the orignal data, green : the fit, yellow : the two merged)

Fitted on i(x,y) = A * exp(-(a*(x-xc)^2 + c*(y-yc)^2 + 2*b*(x-xc)*(y-yc))) + B R^2 = 0.736

Parameters:
A = 304.449 (brightness)
B = 133.254 (background)
a = 0.268 px
b = -0.075 px
c = 1.023 px
xc = 5.681 px
yc = 5.133 px

Z profile & fitting parameters:

Fitted on y = a + (b-a)*exp(-(x-c)^2/(2*d^2)

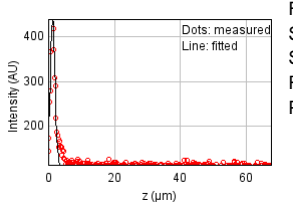
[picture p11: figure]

Sum of residuals squared: 30461.2715 Standard deviation: 9.96104
R^2: 0.95088
Parameters:
a = 112.55352
b = 440.25564
c = 1.38216
d = 0.70782
FWHM | Non corrected | Corrected | Theoretical
min | 361 nm | 373 nm | 223 nm
max | 717 nm | 741 nm | 223 nm
z | 1.67 um | 1.67 um | 885 nm
Asymmetry | 0.503
Theta | -5.6°

Bead 2

Date : Mon Oct 17 13:27:37 PDT 2022
Origin : data_traditional.tif ( Nikon 40x1.15 water ) Frame size : 10 pixels

Coordinates : 113 um (x), 58.6 um (y), 1.55 um (z) Corresponding bead : Not found

XY profile & fitting parameters :
(red : the orignal data, green : the fit, yellow : the two merged)

Fitted on i(x,y) = A * exp(-(a*(x-xc)^2 + c*(y-yc)^2 + 2*b*(x-xc)*(y-yc))) + B R^2 = 0.904

Parameters:
A = 121.007 (brightness)
B = 115.921 (background)
a = 0.176 px
b = -0.030 px
c = 0.424 px

xc = 6.251 px
yc = 6.455 px

Z profile & fitting parameters:

Fitted on y = a + (b-a)*exp(-(x-c)^2/(2*d^2)

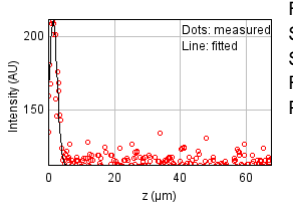
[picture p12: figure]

Sum of residuals squared: 17089.3092 Standard deviation: 7.46093
R^2: 0.83754
Parameters:
a = 111.96087
b = 211.71048
c = 1.55368
d = 1.18975
FWHM | Non corrected | Corrected | Theoretical
min | 560 nm | 579 nm | 223 nm
max | 882 nm | 912 nm | 223 nm
z | 2.8 um | 2.81 um | 885 nm
Asymmetry | 0.635
Theta | -6.8°

Bead 3

Date : Mon Oct 17 13:27:38 PDT 2022
Origin : data_traditional.tif ( Nikon 40x1.15 water ) Frame size : 10 pixels

Coordinates : 126 um (x), 29.1 um (y), 55.3 um (z) Corresponding bead : Not found

XY profile & fitting parameters :
(red : the orignal data, green : the fit, yellow : the two merged)

Fitted on i(x,y) = A * exp(-(a*(x-xc)^2 + c*(y-yc)^2 + 2*b*(x-xc)*(y-yc))) + B R^2 = 0.957

Parameters:
A = 421.938 (brightness)
B = 130.571 (background)
a = 0.300 px
b = 0.095 px
c = 0.113 px

xc = 5.461 px
yc = 6.705 px

Z profile & fitting parameters:

Fitted on y = a + (b-a)*exp(-(x-c)^2/(2*d^2)

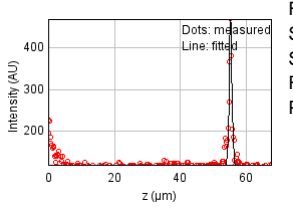
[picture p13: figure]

Sum of residuals squared: 88466.8361 Standard deviation: 16.97544
R^2: 0.82988
Parameters:
a = 116.96598
b = 476.41836
c = 55.30607
d = 0.42400
FWHM | Non corrected | Corrected | Theoretical
min | 629 nm | 650 nm | 223 nm
max | 1.36 um | 1.4 um | 223 nm
z | 998 nm | 1.0 um | 885 nm
Asymmetry | 0.464
Theta | 67.3°

Bead 4

Date : Mon Oct 17 13:27:38 PDT 2022
Origin : data_traditional.tif ( Nikon 40x1.15 water ) Frame size : 10 pixels

Coordinates : 18.6 um (x), 18.7 um (y), 2.74 um (z) Corresponding bead : Not found

XY profile & fitting parameters :
(red : the orignal data, green : the fit, yellow : the two merged)

Fitted on i(x,y) = A * exp(-(a*(x-xc)^2 + c*(y-yc)^2 + 2*b*(x-xc)*(y-yc))) + B R^2 = 0.946

Parameters:
A = 729.309 (brightness)
B = 126.877 (background)
a = 0.731 px
b = -0.048 px
c = 0.487 px

xc = 5.673 px
yc = 7.029 px

Z profile & fitting parameters:

Fitted on y = a + (b-a)*exp(-(x-c)^2/(2*d^2)

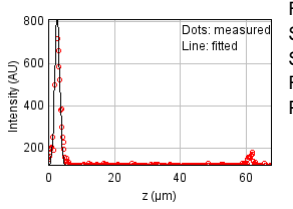
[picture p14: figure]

Sum of residuals squared: 215780.850 Standard deviation: 26.51168
R^2: 0.92945
Parameters:
a = 117.77343
b = 818.08157
c = 2.74127
d = 0.74885
FWHM | Non corrected | Corrected | Theoretical
min | 426 nm | 440 nm | 223 nm
max | 530 nm | 548 nm | 223 nm
z | 1.76 um | 1.77 um | 885 nm
Asymmetry | 0.803
Theta | -79.2°

Bead 5 (Rejected)

Date : Mon Oct 17 13:27:38 PDT 2022
Origin : data_traditional.tif ( Nikon 40x1.15 water ) Frame size : 10 pixels

Coordinates : 126 um (x), -13.5 um (y), 619 nm (z) Corresponding bead : Not found
Reason of rejection : R or C parameter off limits.

XY profile & fitting parameters :
(red : the orignal data, green : the fit, yellow : the two merged)

Fitted on i(x,y) = A * exp(-(a*(x-xc)^2 + c*(y-yc)^2 + 2*b*(x-xc)*(y-yc))) + B R^2 = 0.911

Parameters:
A = 122.160 (brightness)
B = 114.121 (background)
a = 0.211 px
b = -0.383 px
c = 0.875 px
xc = 4.204 px
yc = 5.283 px

Z profile & fitting parameters:

Fitted on y = a + (b-a)*exp(-(x-c)^2/(2*d^2)

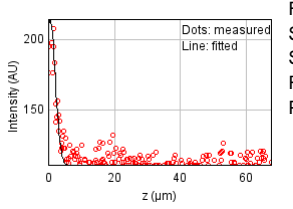
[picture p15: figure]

Sum of residuals squared: 18229.4275 Standard deviation: 7.70579
R^2: 0.83724
Parameters:
a = 111.42863
b = 213.96197
c = 0.61922
d = 1.56438
FWHM | Non corrected | Corrected | Theoretical
min | 358 nm | 370 nm | 223 nm
max | 1.93 um | 2.0 um | 223 nm
z | 3.68 um | 3.7 um | 885 nm
Asymmetry | 0.185
Theta | -24.6°

Bead 6 (Rejected)

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

Coordinates : -23.3 um (x), -42.0 um (y), 2.05 um (z) Corresponding bead : Not found
Reason of rejection : R or C parameter off limits.

XY profile & fitting parameters :
(red : the orignal data, green : the fit, yellow : the two merged)

Fitted on i(x,y) = A * exp(-(a*(x-xc)^2 + c*(y-yc)^2 + 2*b*(x-xc)*(y-yc))) + B R^2 = 0.885

Parameters:
A = 389.323 (brightness)
B = 124.476 (background)
a = 0.393 px
b = 0.053 px
c = 0.347 px
xc = 5.196 px
yc = 5.731 px

Z profile & fitting parameters:

Fitted on y = a + (b-a)*exp(-(x-c)^2/(2*d^2)

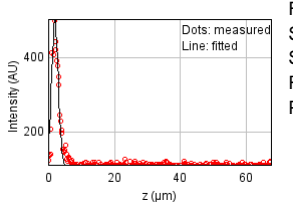
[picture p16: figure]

Sum of residuals squared: 135645.250 Standard deviation: 21.02002
R^2: 0.89406
Parameters:
a = 112.89246
b = 502.35543
c = 2.05183
d = 0.98726
FWHM | Non corrected | Corrected | Theoretical
min | 560 nm | 579 nm | 223 nm
max | 655 nm | 678 nm | 223 nm
z | 2.32 um | 2.33 um | 885 nm
Asymmetry | 0.855
Theta | 56.6°

Bead 7

Date : Mon Oct 17 13:27:39 PDT 2022
Origin : data_traditional.tif ( Nikon 40x1.15 water ) Frame size : 10 pixels

Coordinates : 61.5 um (x), -54.2 um (y), 1.17 um (z) Corresponding bead : Not found

XY profile & fitting parameters :
(red : the orignal data, green : the fit, yellow : the two merged)

Fitted on i(x,y) = A * exp(-(a*(x-xc)^2 + c*(y-yc)^2 + 2*b*(x-xc)*(y-yc))) + B R^2 = 0.962

Parameters:
A = 378.756 (brightness)
B = 123.743 (background)
a = 0.576 px
b = -0.394 px
c = 0.382 px

xc = 5.570 px
yc = 5.589 px

Z profile & fitting parameters:

Fitted on y = a + (b-a)*exp(-(x-c)^2/(2*d^2)

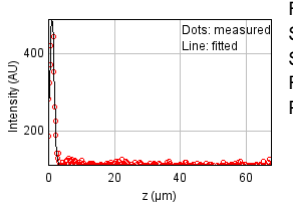
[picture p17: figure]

Sum of residuals squared: 17924.1726 Standard deviation: 7.64100
R^2: 0.97614
Parameters:
a = 112.93988
b = 488.72467
c = 1.16560
d = 0.66887
FWHM | Non corrected | Corrected | Theoretical
min | 389 nm | 403 nm | 223 nm
max | 1.36 um | 1.4 um | 223 nm
z | 1.58 um | 1.58 um | 885 nm
Asymmetry | 0.287
Theta | -51.9°

Bead 8 (Rejected)

Date : Mon Oct 17 13:27:39 PDT 2022
Origin : data_traditional.tif ( Nikon 40x1.15 water ) Frame size : 10 pixels

Coordinates : 85.1 um (x), -93.9 um (y), 4.4 um (z) Corresponding bead : Not found
Reason of rejection : R or C parameter off limits.

XY profile & fitting parameters :
(red : the orignal data, green : the fit, yellow : the two merged)

Fitted on y = a + (b-a)*exp(-(x-c)^2/(2*d^2) Z profile & fitting parameters:

Fitted on y = a + (b-a)*exp(-(x-c)^2/(2*d^2)

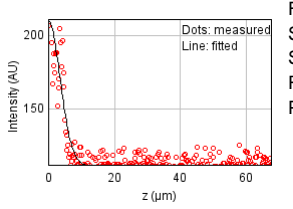
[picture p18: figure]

Sum of residuals squared: 22572.8042 Standard deviation: 8.57479
R^2: 0.85387
Parameters:
a = 112.10265
b = 211.05463
c = -0.028299
d = 3.60399
FWHM | Non corrected | Corrected | Theoretical
min | 0 | 0 | 223 nm
max | 0 | 0 | 223 nm
z | 8.49 um | 8.52 um | 885 nm
Asymmetry | 0.0
Theta | 0.0°

Bead 9 (Rejected)

Date : Mon Oct 17 13:27:39 PDT 2022
Origin : data_traditional.tif ( Nikon 40x1.15 water ) Frame size : 10 pixels

Coordinates : -129 um (x), 93.7 um (y), 1.61 um (z) Corresponding bead : Not found
Reason of rejection : R or C parameter off limits.

XY profile & fitting parameters :
(red : the orignal data, green : the fit, yellow : the two merged)

Fitted on i(x,y) = A * exp(-(a*(x-xc)^2 + c*(y-yc)^2 + 2*b*(x-xc)*(y-yc))) + B R^2 = 0.863

Parameters:
A = 292.052 (brightness)
B = 124.837 (background)
a = 0.404 px
b = -0.140 px
c = 0.683 px
xc = 5.846 px
yc = 5.898 px

Z profile & fitting parameters:

Fitted on y = a + (b-a)*exp(-(x-c)^2/(2*d^2)

Sum of residuals squared: 38061.9694 Standard deviation: 11.13465
R^2: 0.93891
Parameters:
a = 113.48605
b = 408.03827
c = 1.61080
d = 0.87747
FWHM | Non corrected | Corrected | Theoretical
min | 426 nm | 440 nm | 223 nm
max | 622 nm | 644 nm | 223 nm
z | 2.07 um | 2.07 um | 885 nm
Asymmetry | 0.684
Theta | -22.5°

Bead 10

Date : Mon Oct 17 13:27:40 PDT 2022
Origin : data_traditional.tif ( Nikon 40x1.15 water ) Frame size : 10 pixels

Coordinates : -122 um (x), 91.8 um (y), 2.07 um (z) Corresponding bead : Not found

XY profile & fitting parameters :
(red : the orignal data, green : the fit, yellow : the two merged)

Fitted on i(x,y) = A * exp(-(a*(x-xc)^2 + c*(y-yc)^2 + 2*b*(x-xc)*(y-yc))) + B R^2 = 0.910

Parameters:
A = 477.734 (brightness)
B = 132.255 (background)
a = 0.415 px
b = -0.312 px
c = 0.739 px

xc = 6.501 px
yc = 5.911 px

Z profile & fitting parameters:

Fitted on y = a + (b-a)*exp(-(x-c)^2/(2*d^2)

Sum of residuals squared: 72029.2562 Standard deviation: 15.31741
R^2: 0.94887
Parameters:
a = 113.54602
b = 567.54794
c = 2.06943
d = 0.84178
FWHM | Non corrected | Corrected | Theoretical
min | 380 nm | 393 nm | 223 nm
max | 773 nm | 799 nm | 223 nm
z | 1.98 um | 1.99 um | 885 nm
Asymmetry | 0.492
Theta | -31.3°

Bead 11 (Rejected)

Date : Mon Oct 17 13:27:40 PDT 2022
Origin : data_traditional.tif ( Nikon 40x1.15 water ) Frame size : 10 pixels

Coordinates : -132 um (x), 83.6 um (y), 1.98 um (z) Corresponding bead : Not found
Reason of rejection : R or C parameter off limits.

XY profile & fitting parameters :
(red : the orignal data, green : the fit, yellow : the two merged)

Fitted on i(x,y) = A * exp(-(a*(x-xc)^2 + c*(y-yc)^2 + 2*b*(x-xc)*(y-yc))) + B R^2 = 0.900

Parameters:
A = 317.898 (brightness)
B = 124.190 (background)
a = 0.290 px
b = -0.124 px
c = 0.684 px
xc = 5.417 px
yc = 5.782 px

Z profile & fitting parameters:

Fitted on y = a + (b-a)*exp(-(x-c)^2/(2*d^2)

Sum of residuals squared: 40987.5577 Standard deviation: 11.55465
R^2: 0.93925
Parameters:
a = 113.46745
b = 414.49307
c = 1.98085
d = 0.91097
FWHM | Non corrected | Corrected | Theoretical
min | 432 nm | 446 nm | 223 nm
max | 727 nm | 751 nm | 223 nm
z | 2.15 um | 2.15 um | 885 nm
Asymmetry | 0.594
Theta | -16.1°

Bead 12 (Rejected)

Date : Mon Oct 17 13:27:40 PDT 2022
Origin : data_traditional.tif ( Nikon 40x1.15 water ) Frame size : 10 pixels

Coordinates : -159 um (x), 75.0 um (y), 695 nm (z) Corresponding bead : Not found
Reason of rejection : R or C parameter off limits.

XY profile & fitting parameters :
(red : the orignal data, green : the fit, yellow : the two merged)

Fitted on i(x,y) = A * exp(-(a*(x-xc)^2 + c*(y-yc)^2 + 2*b*(x-xc)*(y-yc))) + B R^2 = 0.939

Parameters:
A = 164.780 (brightness)
B = 115.765 (background)
a = 0.066 px
b = -0.086 px
c = 0.922 px
xc = 5.499 px
yc = 4.877 px

Z profile & fitting parameters:

Fitted on y = a + (b-a)*exp(-(x-c)^2/(2*d^2)

Sum of residuals squared: 20393.8639 Standard deviation: 8.15043
R^2: 0.88310
Parameters:
a = 110.96152
b = 244.98184
c = 0.69473
d = 1.41631
FWHM | Non corrected | Corrected | Theoretical
min | 380 nm | 393 nm | 223 nm
max | 1.52 um | 1.57 um | 223 nm
z | 3.34 um | 3.35 um | 885 nm
Asymmetry | 0.25
Theta | -5.7°

Bead 13

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

Coordinates : -25.7 um (x), 71.2 um (y), 1.98 um (z) Corresponding bead : Not found

XY profile & fitting parameters :
(red : the orignal data, green : the fit, yellow : the two merged)

Fitted on i(x,y) = A * exp(-(a*(x-xc)^2 + c*(y-yc)^2 + 2*b*(x-xc)*(y-yc))) + B R^2 = 0.924

Parameters:
A = 432.839 (brightness)
B = 121.403 (background)
a = 0.749 px
b = -0.042 px
c = 0.208 px

xc = 6.119 px
yc = 5.334 px

Z profile & fitting parameters:

Fitted on y = a + (b-a)*exp(-(x-c)^2/(2*d^2)

Sum of residuals squared: 30444.9215 Standard deviation: 9.95837
R^2: 0.97309
Parameters:
a = 113.23840
b = 605.76192
c = 1.97850
d = 0.58094
FWHM | Non corrected | Corrected | Theoretical
min | 422 nm | 437 nm | 223 nm
max | 810 nm | 837 nm | 223 nm
z | 1.37 um | 1.37 um | 885 nm
Asymmetry | 0.522
Theta | -85.6°

Bead 14 (Rejected)

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

Coordinates : -148 um (x), 52.4 um (y), 752 nm (z) Corresponding bead : Not found
Reason of rejection : R or C parameter off limits.

XY profile & fitting parameters :
(red : the orignal data, green : the fit, yellow : the two merged)

Fitted on i(x,y) = A * exp(-(a*(x-xc)^2 + c*(y-yc)^2 + 2*b*(x-xc)*(y-yc))) + B R^2 = 0.896

Parameters:
A = 105.615 (brightness)
B = 114.337 (background)
a = 0.076 px
b = 0.033 px
c = 0.946 px
xc = 5.481 px
yc = 5.911 px

Z profile & fitting parameters:

Fitted on y = a + (b-a)*exp(-(x-c)^2/(2*d^2)

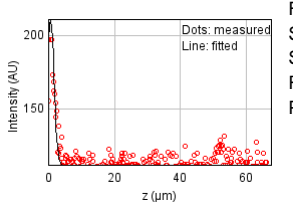
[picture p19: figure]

Sum of residuals squared: 15946.6336 Standard deviation: 7.20718
R^2: 0.81563
Parameters:
a = 111.75890
b = 211.72645
c = 0.75239
d = 1.03409
FWHM | Non corrected | Corrected | Theoretical
min | 376 nm | 389 nm | 223 nm
max | 1.34 um | 1.39 um | 223 nm
z | 2.44 um | 2.44 um | 885 nm
Asymmetry | 0.281
Theta | 2.2°

Bead 15 (Rejected)

Date : Mon Oct 17 13:27:41 PDT 2022
Origin : data_traditional.tif ( Nikon 40x1.15 water ) Frame size : 10 pixels

Coordinates : 146 um (x), 40.7 um (y), 10.2 um (z) Corresponding bead : Not found
Reason of rejection : R or C parameter off limits.

XY profile & fitting parameters :
(red : the orignal data, green : the fit, yellow : the two merged)

Fitted on y = a + (b-a)*exp(-(x-c)^2/(2*d^2) Z profile & fitting parameters:

Fitted on y = a + (b-a)*exp(-(x-c)^2/(2*d^2)

Sum of residuals squared: 44805.6211 Standard deviation: 12.08084
R^2: 0.56284
Parameters:
a = 113.14624
b = 210.71166
c = 10.24275
d = 0.78439
FWHM | Non corrected | Corrected | Theoretical
min | 0 | 0 | 223 nm
max | 0 | 0 | 223 nm
z | 1.85 um | 1.85 um | 885 nm
Asymmetry | 0.0
Theta | 0.0°

Bead 16 (Rejected)

Date : Mon Oct 17 13:27:41 PDT 2022
Origin : data_traditional.tif ( Nikon 40x1.15 water ) Frame size : 10 pixels

Coordinates : 126 um (x), 40.1 um (y), 928 nm (z) Corresponding bead : Not found
Reason of rejection : R or C parameter off limits.

XY profile & fitting parameters :
(red : the orignal data, green : the fit, yellow : the two merged)

Fitted on i(x,y) = A * exp(-(a*(x-xc)^2 + c*(y-yc)^2 + 2*b*(x-xc)*(y-yc))) + B R^2 = 0.927

Parameters:
A = 114.813 (brightness)
B = 111.762 (background)
a = 0.090 px
b = -0.190 px
c = 0.874 px
xc = 4.716 px
yc = 5.756 px

Z profile & fitting parameters:

Fitted on y = a + (b-a)*exp(-(x-c)^2/(2*d^2)

Sum of residuals squared: 18969.7295 Standard deviation: 7.86070
R^2: 0.82108
Parameters:
a = 111.42118
b = 212.09285
c = 0.92760
d = 1.28032
FWHM | Non corrected | Corrected | Theoretical
min | 383 nm | 395 nm | 223 nm
max | 1.7 um | 1.76 um | 223 nm
z | 3.01 um | 3.03 um | 885 nm
Asymmetry | 0.225
Theta | -12.9°

Bead 17 (Rejected)

Date : Mon Oct 17 13:27:41 PDT 2022
Origin : data_traditional.tif ( Nikon 40x1.15 water ) Frame size : 10 pixels

Coordinates : -66.1 um (x), 31.7 um (y), 227 nm (z)
Corresponding bead : Not found
Reason of rejection : The fitted bead is likely to be a different bead from the center bead.

XY profile & fitting parameters :
(red : the orignal data, green : the fit, yellow : the two merged)

Fitted on i(x,y) = A * exp(-(a*(x-xc)^2 + c*(y-yc)^2 + 2*b*(x-xc)*(y-yc))) + B R^2 = 0.508

Parameters:
A = -71.114 (brightness)
B = 197.931 (background)
a = 0.022 px
b = -0.034 px
c = 0.018 px
xc = 1.498 px
yc = 6.809 px

Z profile & fitting parameters:

Fitted on y = a + (b-a)*exp(-(x-c)^2/(2*d^2)

Sum of residuals squared: 19162.0657 Standard deviation: 7.90045
R^2: 0.75620
Parameters:
a = 112.47102
b = 192.29539
c = 0.22723
d = 2.08255
FWHM | Non corrected | Corrected | Theoretical
min | 1.58 um | 1.63 um | 223 nm
max | 3.15 um | 3.26 um | 223 nm
z | 4.9 um | 4.92 um | 885 nm
Asymmetry | 0.501
Theta | 0.0°

Bead 18

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

Coordinates : 48.3 um (x), 7.83 um (y), 2.33 um (z) Corresponding bead : Not found

XY profile & fitting parameters :
(red : the orignal data, green : the fit, yellow : the two merged)

Fitted on i(x,y) = A * exp(-(a*(x-xc)^2 + c*(y-yc)^2 + 2*b*(x-xc)*(y-yc))) + B R^2 = 0.954

Parameters:
A = 1076.922 (brightness)
B = 133.567 (background)
a = 0.738 px
b = -0.128 px
c = 0.548 px

xc = 5.356 px
yc = 6.388 px

Z profile & fitting parameters:

Fitted on y = a + (b-a)*exp(-(x-c)^2/(2*d^2)

Sum of residuals squared: 109505.400 Standard deviation: 18.88637
R^2: 0.97649
Parameters:
a = 116.22996
b = 1147.15000
c = 2.33208
d = 0.54675
FWHM | Non corrected | Corrected | Theoretical
min | 409 nm | 423 nm | 223 nm
max | 527 nm | 545 nm | 223 nm
z | 1.29 um | 1.29 um | 885 nm
Asymmetry | 0.776
Theta | -63.3°

Bead 19

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

Coordinates : -21.0 um (x), 5.05 um (y), 49.9 um (z) Corresponding bead : Not found

XY profile & fitting parameters :
(red : the orignal data, green : the fit, yellow : the two merged)

Fitted on i(x,y) = A * exp(-(a*(x-xc)^2 + c*(y-yc)^2 + 2*b*(x-xc)*(y-yc))) + B R^2 = 0.987

Parameters:
A = 2206.553 (brightness)
B = 130.669 (background)
a = 0.831 px
b = 0.011 px
c = 0.503 px

xc = 4.578 px
yc = 4.046 px

Z profile & fitting parameters:

Fitted on y = a + (b-a)*exp(-(x-c)^2/(2*d^2)

Sum of residuals squared: 467443.209 Standard deviation: 39.02072
R^2: 0.96870
Parameters:
a = 123.59721
b = 2121.67945
c = 49.90449
d = 0.46083
FWHM | Non corrected | Corrected | Theoretical
min | 402 nm | 415 nm | 223 nm
max | 517 nm | 534 nm | 223 nm
z | 1.09 um | 1.09 um | 885 nm
Asymmetry | 0.778
Theta | 88.1°

Bead 20 (Rejected)

Date : Mon Oct 17 13:27:42 PDT 2022
Origin : data_traditional.tif ( Nikon 40x1.15 water ) Frame size : 10 pixels

Coordinates : 126 um (x), -13.5 um (y), 619 nm (z) Corresponding bead : Not found
Reason of rejection : R or C parameter off limits.

XY profile & fitting parameters :
(red : the orignal data, green : the fit, yellow : the two merged)

Fitted on i(x,y) = A * exp(-(a*(x-xc)^2 + c*(y-yc)^2 + 2*b*(x-xc)*(y-yc))) + B R^2 = 0.899

Parameters:
A = 124.788 (brightness)
B = 114.238 (background)
a = 0.233 px
b = -0.396 px
c = 0.868 px
xc = 6.054 px
yc = 5.229 px

Z profile & fitting parameters:

Fitted on y = a + (b-a)*exp(-(x-c)^2/(2*d^2)

Sum of residuals squared: 18229.4275 Standard deviation: 7.70579
R^2: 0.83724
Parameters:
a = 111.42863
b = 213.96197
c = 0.61922
d = 1.56438
FWHM | Non corrected | Corrected | Theoretical
min | 356 nm | 368 nm | 223 nm
max | 1.77 um | 1.83 um | 223 nm
z | 3.68 um | 3.7 um | 885 nm
Asymmetry | 0.201
Theta | -25.6°

Bead 21 (Rejected)

Date : Mon Oct 17 13:27:42 PDT 2022
Origin : data_traditional.tif ( Nikon 40x1.15 water ) Frame size : 10 pixels

Coordinates : 55.5 um (x), -39.1 um (y), 1.89 um (z)
Corresponding bead : Not found
Reason of rejection : The fitted bead is likely to be a different bead from the center bead.

XY profile & fitting parameters :
(red : the orignal data, green : the fit, yellow : the two merged)

Fitted on i(x,y) = A * exp(-(a*(x-xc)^2 + c*(y-yc)^2 + 2*b*(x-xc)*(y-yc))) + B R^2 = 0.942

Parameters:
A = 602.045 (brightness)
B = 128.841 (background)
a = 0.570 px
b = -0.199 px
c = 0.336 px
xc = 6.161 px
yc = 4.940 px

Z profile & fitting parameters:

Fitted on y = a + (b-a)*exp(-(x-c)^2/(2*d^2)

Sum of residuals squared: 50714.3329 Standard deviation: 12.85275
R^2: 0.88668
Parameters:
a = 115.34282
b = 398.08103
c = 1.88782
d = 0.63732
FWHM | Non corrected | Corrected | Theoretical
min | 443 nm | 458 nm | 223 nm
max | 777 nm | 804 nm | 223 nm
z | 1.5 um | 1.51 um | 885 nm
Asymmetry | 0.57
Theta | -60.2°

Bead 22 (Rejected)

Date : Mon Oct 17 13:27:42 PDT 2022
Origin : data_traditional.tif ( Nikon 40x1.15 water ) Frame size : 10 pixels

Coordinates : 55.5 um (x), -39.1 um (y), 1.89 um (z)
Corresponding bead : Not found
Reason of rejection : The fitted bead is likely to be a different bead from the center bead.

XY profile & fitting parameters :
(red : the orignal data, green : the fit, yellow : the two merged)

Fitted on i(x,y) = A * exp(-(a*(x-xc)^2 + c*(y-yc)^2 + 2*b*(x-xc)*(y-yc))) + B R^2 = 0.949

Parameters:
A = 604.122 (brightness)
B = 126.114 (background)
a = 0.562 px
b = -0.192 px
c = 0.330 px
xc = 7.157 px
yc = 4.937 px

Z profile & fitting parameters:

Fitted on y = a + (b-a)*exp(-(x-c)^2/(2*d^2)

Sum of residuals squared: 50714.3329 Standard deviation: 12.85275
R^2: 0.88668
Parameters:
a = 115.34282
b = 398.08103
c = 1.88782
d = 0.63732
FWHM | Non corrected | Corrected | Theoretical
min | 448 nm | 463 nm | 223 nm
max | 778 nm | 804 nm | 223 nm
z | 1.5 um | 1.51 um | 885 nm
Asymmetry | 0.576
Theta | -60.5°

Bead 23

Date : Mon Oct 17 13:27:43 PDT 2022
Origin : data_traditional.tif ( Nikon 40x1.15 water ) Frame size : 10 pixels

Coordinates : 63.4 um (x), -50.3 um (y), 1.79 um (z) Corresponding bead : Not found

XY profile & fitting parameters :
(red : the orignal data, green : the fit, yellow : the two merged)

Fitted on i(x,y) = A * exp(-(a*(x-xc)^2 + c*(y-yc)^2 + 2*b*(x-xc)*(y-yc))) + B R^2 = 0.924

Parameters:
A = 263.553 (brightness)
B = 126.504 (background)
a = 0.444 px
b = -0.277 px
c = 0.373 px

xc = 6.091 px
yc = 5.645 px

Z profile & fitting parameters:

Fitted on y = a + (b-a)*exp(-(x-c)^2/(2*d^2)

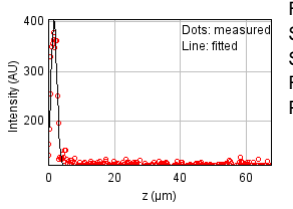
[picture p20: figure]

Sum of residuals squared: 29682.4071 Standard deviation: 9.83287
R^2: 0.95120
Parameters:
a = 112.16554
b = 403.66400
c = 1.79079
d = 0.88590
FWHM | Non corrected | Corrected | Theoretical
min | 442 nm | 457 nm | 223 nm
max | 1.02 um | 1.05 um | 223 nm
z | 2.09 um | 2.09 um | 885 nm
Asymmetry | 0.434
Theta | -48.6°

Bead 24 (Rejected)

Date : Mon Oct 17 13:27:43 PDT 2022
Origin : data_traditional.tif ( Nikon 40x1.15 water ) Frame size : 10 pixels

Coordinates : -39.2 um (x), -56.3 um (y), 925 nm (z) Corresponding bead : Not found
Reason of rejection : R or C parameter off limits.

XY profile & fitting parameters :
(red : the orignal data, green : the fit, yellow : the two merged)

Fitted on y = a + (b-a)*exp(-(x-c)^2/(2*d^2) Z profile & fitting parameters:

Fitted on y = a + (b-a)*exp(-(x-c)^2/(2*d^2)

Sum of residuals squared: 14388.8608 Standard deviation: 6.84611
R^2: 0.78180
Parameters:
a = 114.30370
b = 200.25899
c = 0.92531
d = 0.96297
FWHM | Non corrected | Corrected | Theoretical
min | 0 | 0 | 223 nm
max | 0 | 0 | 223 nm
z | 2.27 um | 2.28 um | 885 nm
Asymmetry | 0.0
Theta | 0.0°

Bead 25 (Rejected)

Date : Mon Oct 17 13:27:43 PDT 2022
Origin : data_traditional.tif ( Nikon 40x1.15 water ) Frame size : 10 pixels

Coordinates : 74.4 um (x), -74.3 um (y), 2.92 um (z)
Corresponding bead : Not found
Reason of rejection : The fitted bead is likely to be a different bead from the center bead.

XY profile & fitting parameters :
(red : the orignal data, green : the fit, yellow : the two merged)

Fitted on i(x,y) = A * exp(-(a*(x-xc)^2 + c*(y-yc)^2 + 2*b*(x-xc)*(y-yc))) + B R^2 = 0.758

Parameters:
A = 115.134 (brightness)
B = 134.511 (background)
a = 0.145 px
b = 0.113 px
c = 0.287 px
xc = 6.319 px
yc = 6.794 px

Z profile & fitting parameters:

Fitted on y = a + (b-a)*exp(-(x-c)^2/(2*d^2)

Sum of residuals squared: 17347.8437 Standard deviation: 7.51716
R^2: 0.69874
Parameters:
a = 114.33285
b = 204.92692
c = 2.91592
d = 0.62922
FWHM | Non corrected | Corrected | Theoretical
min | 620 nm | 641 nm | 223 nm
max | 1.28 um | 1.32 um | 223 nm
z | 1.48 um | 1.49 um | 885 nm
Asymmetry | 0.486
Theta | 28.9°

Bead 26 (Rejected)

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

Coordinates : -149 um (x), 75.9 um (y), 2.53 um (z) Corresponding bead : Not found
Reason of rejection : R or C parameter off limits.

XY profile & fitting parameters :
(red : the orignal data, green : the fit, yellow : the two merged)

Fitted on i(x,y) = A * exp(-(a*(x-xc)^2 + c*(y-yc)^2 + 2*b*(x-xc)*(y-yc))) + B R^2 = 0.807

Parameters:
A = 91.022 (brightness)
B = 115.338 (background)
a = 0.459 px
b = 0.086 px
c = 0.182 px
xc = 5.213 px
yc = 6.981 px

Z profile & fitting parameters:

Fitted on y = a + (b-a)*exp(-(x-c)^2/(2*d^2)

Sum of residuals squared: 13675.9845 Standard deviation: 6.67437
R^2: 0.80898
Parameters:
a = 111.28687
b = 195.27832
c = 2.53376
d = 1.07939
FWHM | Non corrected | Corrected | Theoretical
min | 527 nm | 545 nm | 223 nm
max | 923 nm | 954 nm | 223 nm
z | 2.54 um | 2.55 um | 885 nm
Asymmetry | 0.571
Theta | 74.1°

Bead 27 (Rejected)

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

Coordinates : -11.9 um (x), 73.3 um (y), 47.7 um (z) Corresponding bead : Not found
Reason of rejection : R or C parameter off limits.

XY profile & fitting parameters :
(red : the orignal data, green : the fit, yellow : the two merged)

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

Fitted on y = a + (b-a)*exp(-(x-c)^2/(2*d^2)

Sum of residuals squared: 383909.252 Standard deviation: 35.36267
R^2: 0.87515
Parameters:
a = 122.02903
b = 778.43438
c = 47.71187
d = 0.80948
FWHM | Non corrected | Corrected | Theoretical
min | 0 | 0 | 223 nm
max | 0 | 0 | 223 nm
z | 1.91 um | 1.91 um | 885 nm
Asymmetry | 0.0
Theta | 0.0°

Bead 28

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

Coordinates : -68.7 um (x), 37.5 um (y), 3.06 um (z) Corresponding bead : Not found

XY profile & fitting parameters :
(red : the orignal data, green : the fit, yellow : the two merged)

Fitted on i(x,y) = A * exp(-(a*(x-xc)^2 + c*(y-yc)^2 + 2*b*(x-xc)*(y-yc))) + B R^2 = 0.918

Parameters:
A = 445.923 (brightness)
B = 126.425 (background)
a = 0.457 px
b = 0.101 px
c = 0.672 px

xc = 5.781 px
yc = 6.528 px

Z profile & fitting parameters:

Fitted on y = a + (b-a)*exp(-(x-c)^2/(2*d^2)

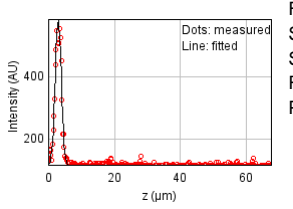
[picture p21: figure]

Sum of residuals squared: 40543.6708 Standard deviation: 11.49191
R^2: 0.97435
Parameters:
a = 114.45302
b = 584.03270
c = 3.06279
d = 0.91035
FWHM | Non corrected | Corrected | Theoretical
min | 434 nm | 449 nm | 223 nm
max | 567 nm | 586 nm | 223 nm
z | 2.14 um | 2.15 um | 885 nm
Asymmetry | 0.765
Theta | 21.5°

Bead 29

Date : Mon Oct 17 13:27:44 PDT 2022
Origin : data_traditional.tif ( Nikon 40x1.15 water ) Frame size : 10 pixels

Coordinates : 95.0 um (x), 36.5 um (y), 2.15 um (z) Corresponding bead : Not found

XY profile & fitting parameters :
(red : the orignal data, green : the fit, yellow : the two merged)

Fitted on i(x,y) = A * exp(-(a*(x-xc)^2 + c*(y-yc)^2 + 2*b*(x-xc)*(y-yc))) + B R^2 = 0.945

Parameters:
A = 356.790 (brightness)
B = 119.077 (background)
a = 0.164 px
b = -0.128 px
c = 0.980 px

xc = 5.604 px
yc = 6.245 px

Z profile & fitting parameters:

Fitted on y = a + (b-a)*exp(-(x-c)^2/(2*d^2)

Sum of residuals squared: 35952.2699 Standard deviation: 10.82166
R^2: 0.95060
Parameters:
a = 112.91007
b = 450.56411
c = 2.15229
d = 0.78539
FWHM | Non corrected | Corrected | Theoretical
min | 366 nm | 379 nm | 223 nm
max | 965 nm | 998 nm | 223 nm
z | 1.85 um | 1.86 um | 885 nm
Asymmetry | 0.38
Theta | -8.7°

Bead 30

Date : Mon Oct 17 13:27:44 PDT 2022
Origin : data_traditional.tif ( Nikon 40x1.15 water ) Frame size : 10 pixels

Coordinates : -107 um (x), -4.38 um (y), 2.63 um (z) Corresponding bead : Not found

XY profile & fitting parameters :
(red : the orignal data, green : the fit, yellow : the two merged)

Fitted on i(x,y) = A * exp(-(a*(x-xc)^2 + c*(y-yc)^2 + 2*b*(x-xc)*(y-yc))) + B R^2 = 0.966

Parameters:
A = 725.272 (brightness)
B = 130.795 (background)
a = 0.521 px
b = 0.099 px
c = 0.565 px

xc = 6.047 px
yc = 5.895 px

Z profile & fitting parameters:

Fitted on y = a + (b-a)*exp(-(x-c)^2/(2*d^2)

Sum of residuals squared: 47652.9894 Standard deviation: 12.45879
R^2: 0.98401
Parameters:
a = 113.47064
b = 857.83313
c = 2.62677
d = 0.68142
FWHM | Non corrected | Corrected | Theoretical
min | 457 nm | 472 nm | 223 nm
max | 551 nm | 570 nm | 223 nm
z | 1.6 um | 1.61 um | 885 nm
Asymmetry | 0.829
Theta | 38.8°

Bead 31 (Rejected)

Date : Mon Oct 17 13:27:44 PDT 2022
Origin : data_traditional.tif ( Nikon 40x1.15 water ) Frame size : 10 pixels

Coordinates : -22.2 um (x), -10.8 um (y), 2.28 um (z) Corresponding bead : Not found
Reason of rejection : R or C parameter off limits.

XY profile & fitting parameters :
(red : the orignal data, green : the fit, yellow : the two merged)

Fitted on i(x,y) = A * exp(-(a*(x-xc)^2 + c*(y-yc)^2 + 2*b*(x-xc)*(y-yc))) + B R^2 = 0.817

Parameters:
A = 589.080 (brightness)
B = 141.303 (background)
a = 0.785 px
b = 0.080 px
c = 0.280 px
xc = 6.199 px
yc = 5.179 px

Z profile & fitting parameters:

Fitted on y = a + (b-a)*exp(-(x-c)^2/(2*d^2)

Sum of residuals squared: 64408.4684 Standard deviation: 14.48446
R^2: 0.96935
Parameters:
a = 113.64361
b = 787.81659
c = 2.28377
d = 0.57344
FWHM | Non corrected | Corrected | Theoretical
min | 410 nm | 424 nm | 223 nm
max | 708 nm | 731 nm | 223 nm
z | 1.35 um | 1.36 um | 885 nm
Asymmetry | 0.58
Theta | 81.2°

Bead 32

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

Coordinates : -61.8 um (x), -27.5 um (y), 2.5 um (z) Corresponding bead : Not found

XY profile & fitting parameters :
(red : the orignal data, green : the fit, yellow : the two merged)

Fitted on i(x,y) = A * exp(-(a*(x-xc)^2 + c*(y-yc)^2 + 2*b*(x-xc)*(y-yc))) + B R^2 = 0.900

Parameters:
A = 922.608 (brightness)
B = 148.497 (background)
a = 0.773 px
b = 0.064 px
c = 0.545 px

xc = 6.216 px
yc = 5.055 px

Z profile & fitting parameters:

Fitted on y = a + (b-a)*exp(-(x-c)^2/(2*d^2)

Sum of residuals squared: 109978.173 Standard deviation: 18.92710
R^2: 0.97010
Parameters:
a = 114.93016
b = 967.20937
c = 2.50346
d = 0.63050
FWHM | Non corrected | Corrected | Theoretical
min | 412 nm | 426 nm | 223 nm
max | 504 nm | 521 nm | 223 nm
z | 1.48 um | 1.49 um | 885 nm
Asymmetry | 0.818
Theta | 75.4°

Bead 33 (Rejected)

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

Coordinates : 105 um (x), -75.2 um (y), 1.64 um (z)
Corresponding bead : Not found
Reason of rejection : The fitted bead is likely to be a different bead from the center bead.

XY profile & fitting parameters :
(red : the orignal data, green : the fit, yellow : the two merged)

Fitted on i(x,y) = A * exp(-(a*(x-xc)^2 + c*(y-yc)^2 + 2*b*(x-xc)*(y-yc))) + B R^2 = 0.907

Parameters:
A = 104.443 (brightness)
B = 117.081 (background)
a = 0.396 px
b = -0.386 px
c = 0.408 px
xc = 6.053 px
yc = 5.914 px

Z profile & fitting parameters:

Fitted on y = a + (b-a)*exp(-(x-c)^2/(2*d^2)

Sum of residuals squared: 12018.3222 Standard deviation: 6.25681
R^2: 0.86031
Parameters:
a = 111.75830
b = 220.40702
c = 1.63823
d = 0.81266
FWHM | Non corrected | Corrected | Theoretical
min | 413 nm | 427 nm | 223 nm
max | 2.95 um | 3.05 um | 223 nm
z | 1.91 um | 1.92 um | 885 nm
Asymmetry | 0.14
Theta | -44.6°

Bead 34 (Rejected)

Date : Mon Oct 17 13:27:45 PDT 2022
Origin : data_traditional.tif ( Nikon 40x1.15 water ) Frame size : 10 pixels

Coordinates : 126 um (x), 40.1 um (y), 928 nm (z) Corresponding bead : Not found
Reason of rejection : R or C parameter off limits.

XY profile & fitting parameters :
(red : the orignal data, green : the fit, yellow : the two merged)

Fitted on i(x,y) = A * exp(-(a*(x-xc)^2 + c*(y-yc)^2 + 2*b*(x-xc)*(y-yc))) + B R^2 = 0.927

Parameters:
A = 114.813 (brightness)
B = 111.762 (background)
a = 0.090 px
b = -0.190 px
c = 0.874 px
xc = 4.716 px
yc = 5.756 px

Z profile & fitting parameters:

Fitted on y = a + (b-a)*exp(-(x-c)^2/(2*d^2)

Sum of residuals squared: 18969.7295 Standard deviation: 7.86070
R^2: 0.82108
Parameters:
a = 111.42118
b = 212.09285
c = 0.92760
d = 1.28032
FWHM | Non corrected | Corrected | Theoretical
min | 383 nm | 395 nm | 223 nm
max | 1.7 um | 1.76 um | 223 nm
z | 3.01 um | 3.03 um | 885 nm
Asymmetry | 0.225
Theta | -12.9°

Bead 35 (Rejected)

Date : Mon Oct 17 13:27:45 PDT 2022
Origin : data_traditional.tif ( Nikon 40x1.15 water ) Frame size : 10 pixels

Coordinates : -86.4 um (x), 25.1 um (y), 3.14 um (z) Corresponding bead : Not found
Reason of rejection : R or C parameter off limits.

XY profile & fitting parameters :
(red : the orignal data, green : the fit, yellow : the two merged)

Fitted on i(x,y) = A * exp(-(a*(x-xc)^2 + c*(y-yc)^2 + 2*b*(x-xc)*(y-yc))) + B R^2 = 0.899

Parameters:
A = 659.397 (brightness)
B = 134.265 (background)
a = 0.726 px
b = 0.158 px
c = 0.757 px
xc = 5.419 px
yc = 6.109 px

Z profile & fitting parameters:

Fitted on y = a + (b-a)*exp(-(x-c)^2/(2*d^2)

Sum of residuals squared: 45156.9119 Standard deviation: 12.12810
R^2: 0.97527
Parameters:
a = 114.98952
b = 602.35461
c = 3.14162
d = 0.98068
FWHM | Non corrected | Corrected | Theoretical
min | 386 nm | 399 nm | 223 nm
max | 480 nm | 496 nm | 223 nm
z | 2.31 um | 2.32 um | 885 nm
Asymmetry | 0.805
Theta | 42.2°

Bead 36 (Rejected)

Date : Mon Oct 17 13:27:45 PDT 2022
Origin : data_traditional.tif ( Nikon 40x1.15 water ) Frame size : 10 pixels

Coordinates : -142 um (x), 22.7 um (y), 3.09 um (z) Corresponding bead : Not found
Reason of rejection : R or C parameter off limits.

XY profile & fitting parameters :
(red : the orignal data, green : the fit, yellow : the two merged)

Fitted on i(x,y) = A * exp(-(a*(x-xc)^2 + c*(y-yc)^2 + 2*b*(x-xc)*(y-yc))) + B R^2 = 0.839

Parameters:
A = 116.304 (brightness)
B = 121.313 (background)
a = 0.285 px
b = 0.002 px
c = 0.226 px
xc = 5.064 px
yc = 6.902 px

Z profile & fitting parameters:

Fitted on y = a + (b-a)*exp(-(x-c)^2/(2*d^2)

Sum of residuals squared: 35374.8576 Standard deviation: 10.73441
R^2: 0.89049
Parameters:
a = 111.75620
b = 266.13208
c = 3.09279
d = 1.63571
FWHM | Non corrected | Corrected | Theoretical
min | 686 nm | 709 nm | 223 nm
max | 771 nm | 797 nm | 223 nm
z | 3.85 um | 3.87 um | 885 nm
Asymmetry | 0.889
Theta | 88.4°

Bead 37 (Rejected)

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

Coordinates : 164 um (x), 23.4 um (y), 864 nm (z)
Corresponding bead : Not found
Reason of rejection : The fitted bead is likely to be a different bead from the center bead.

XY profile & fitting parameters :
(red : the orignal data, green : the fit, yellow : the two merged)

Fitted on i(x,y) = A * exp(-(a*(x-xc)^2 + c*(y-yc)^2 + 2*b*(x-xc)*(y-yc))) + B R^2 = 0.835

Parameters:
A = 80.764 (brightness)
B = 118.030 (background)
a = 0.082 px
b = -0.214 px
c = 0.836 px
xc = 4.885 px
yc = 5.556 px

Z profile & fitting parameters:

Fitted on y = a + (b-a)*exp(-(x-c)^2/(2*d^2)

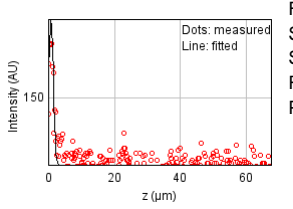
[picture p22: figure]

Sum of residuals squared: 12654.1608 Standard deviation: 6.42018
R^2: 0.75268
Parameters:
a = 110.73638
b = 195.48383
c = 0.86432
d = 0.70455
FWHM | Non corrected | Corrected | Theoretical
min | 388 nm | 401 nm | 223 nm
max | 2.29 um | 2.37 um | 223 nm
z | 1.66 um | 1.67 um | 885 nm
Asymmetry | 0.169
Theta | -14.8°

Bead 38 (Rejected)

Date : Mon Oct 17 13:27:46 PDT 2022
Origin : data_traditional.tif ( Nikon 40x1.15 water ) Frame size : 10 pixels

Coordinates : 55.7 um (x), -39.5 um (y), 3.72 um (z)
Corresponding bead : Not found
Reason of rejection : The fitted bead is likely to be a different bead from the center bead.

XY profile & fitting parameters :
(red : the orignal data, green : the fit, yellow : the two merged)

Fitted on i(x,y) = A * exp(-(a*(x-xc)^2 + c*(y-yc)^2 + 2*b*(x-xc)*(y-yc))) + B R^2 = 0.968

Parameters:
A = 241.866 (brightness)
B = 120.283 (background)
a = 0.295 px
b = 0.355 px
c = 0.627 px
xc = 3.995 px
yc = 6.626 px

Z profile & fitting parameters:

Fitted on y = a + (b-a)*exp(-(x-c)^2/(2*d^2)

Sum of residuals squared: 47724.8309 Standard deviation: 12.46818
R^2: 0.68387
Parameters:
a = 115.80875
b = 250.43406
c = 3.71969
d = 0.73532
FWHM | Non corrected | Corrected | Theoretical
min | 397 nm | 410 nm | 223 nm
max | 1.39 um | 1.44 um | 223 nm
z | 1.73 um | 1.74 um | 885 nm
Asymmetry | 0.285
Theta | 32.5°

Bead 39

Date : Mon Oct 17 13:27:46 PDT 2022
Origin : data_traditional.tif ( Nikon 40x1.15 water ) Frame size : 10 pixels

Coordinates : 112 um (x), -49.6 um (y), 1.16 um (z) Corresponding bead : Not found

XY profile & fitting parameters :
(red : the orignal data, green : the fit, yellow : the two merged)

Fitted on i(x,y) = A * exp(-(a*(x-xc)^2 + c*(y-yc)^2 + 2*b*(x-xc)*(y-yc))) + B R^2 = 0.916

Parameters:
A = 147.347 (brightness)
B = 114.993 (background)
a = 0.414 px
b = -0.475 px
c = 0.644 px

xc = 6.567 px
yc = 5.522 px

Z profile & fitting parameters:

Fitted on y = a + (b-a)*exp(-(x-c)^2/(2*d^2)

Sum of residuals squared: 17775.8499 Standard deviation: 7.60932
R^2: 0.87250
Parameters:
a = 111.35191
b = 271.55815
c = 1.15972
d = 0.60777
FWHM | Non corrected | Corrected | Theoretical
min | 363 nm | 375 nm | 223 nm
max | 1.82 um | 1.88 um | 223 nm
z | 1.43 um | 1.44 um | 885 nm
Asymmetry | 0.199
Theta | -38.2°

Bead 40 (Rejected)

Date : Mon Oct 17 13:27:46 PDT 2022
Origin : data_traditional.tif ( Nikon 40x1.15 water ) Frame size : 10 pixels

Coordinates : 38.9 um (x), -76.8 um (y), 594 nm (z) Corresponding bead : Not found
Reason of rejection : R or C parameter off limits.

XY profile & fitting parameters :
(red : the orignal data, green : the fit, yellow : the two merged)

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

Fitted on y = a + (b-a)*exp(-(x-c)^2/(2*d^2)

Sum of residuals squared: 12565.4239 Standard deviation: 6.39763
R^2: 0.84092
Parameters:
a = 112.81749
b = 221.82157
c = 0.59436
d = 0.79997
FWHM | Non corrected | Corrected | Theoretical
min | 0 | 0 | 223 nm
max | 0 | 0 | 223 nm
z | 1.88 um | 1.89 um | 885 nm
Asymmetry | 0.0
Theta | 0.0°

Bead 41 (Rejected)

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

Coordinates : -98.1 um (x), -87.2 um (y), 1.66 um (z) Corresponding bead : Not found
Reason of rejection : R or C parameter off limits.

XY profile & fitting parameters :
(red : the orignal data, green : the fit, yellow : the two merged)

Fitted on i(x,y) = A * exp(-(a*(x-xc)^2 + c*(y-yc)^2 + 2*b*(x-xc)*(y-yc))) + B R^2 = 0.795

Parameters:
A = 64.820 (brightness)
B = 124.383 (background)
a = 0.096 px
b = -0.127 px
c = 0.320 px
xc = 5.259 px
yc = 5.373 px

Z profile & fitting parameters:

Fitted on y = a + (b-a)*exp(-(x-c)^2/(2*d^2)

Sum of residuals squared: 19706.5252 Standard deviation: 8.01191
R^2: 0.84038
Parameters:
a = 111.13012
b = 213.38708
c = 1.66427
d = 1.35264
FWHM | Non corrected | Corrected | Theoretical
min | 596 nm | 616 nm | 223 nm
max | 1.86 um | 1.93 um | 223 nm
z | 3.19 um | 3.2 um | 885 nm
Asymmetry | 0.32
Theta | -24.3°

Bead 42

Date : Mon Oct 17 13:27:47 PDT 2022
Origin : data_traditional.tif ( Nikon 40x1.15 water ) Frame size : 10 pixels

Coordinates : 51.0 um (x), 74.8 um (y), 2.73 um (z) Corresponding bead : Not found

XY profile & fitting parameters :
(red : the orignal data, green : the fit, yellow : the two merged)

Fitted on i(x,y) = A * exp(-(a*(x-xc)^2 + c*(y-yc)^2 + 2*b*(x-xc)*(y-yc))) + B R^2 = 0.966

Parameters:
A = 924.902 (brightness)
B = 126.483 (background)
a = 0.747 px
b = 0.065 px
c = 0.486 px

xc = 5.917 px
yc = 5.980 px

Z profile & fitting parameters:

Fitted on y = a + (b-a)*exp(-(x-c)^2/(2*d^2)

Sum of residuals squared: 69825.2062 Standard deviation: 15.08124
R^2: 0.98361
Parameters:
a = 115.19085
b = 1080.00866
c = 2.73310
d = 0.57612
FWHM | Non corrected | Corrected | Theoretical
min | 420 nm | 434 nm | 223 nm
max | 534 nm | 552 nm | 223 nm
z | 1.36 um | 1.36 um | 885 nm
Asymmetry | 0.786
Theta | 76.7°

Bead 43

Date : Mon Oct 17 13:27:47 PDT 2022
Origin : data_traditional.tif ( Nikon 40x1.15 water ) Frame size : 10 pixels

Coordinates : -118 um (x), 33.7 um (y), 2.99 um (z) Corresponding bead : Not found

XY profile & fitting parameters :
(red : the orignal data, green : the fit, yellow : the two merged)

Fitted on i(x,y) = A * exp(-(a*(x-xc)^2 + c*(y-yc)^2 + 2*b*(x-xc)*(y-yc))) + B R^2 = 0.951

Parameters:
A = 347.143 (brightness)
B = 120.917 (background)
a = 0.420 px
b = 0.048 px
c = 0.648 px

xc = 5.795 px
yc = 5.897 px

Z profile & fitting parameters:

Fitted on y = a + (b-a)*exp(-(x-c)^2/(2*d^2)

Sum of residuals squared: 29897.1999 Standard deviation: 9.86838
R^2: 0.96823
Parameters:
a = 112.03458
b = 510.76924
c = 2.99332
d = 0.73989
FWHM | Non corrected | Corrected | Theoretical
min | 452 nm | 467 nm | 223 nm
max | 572 nm | 591 nm | 223 nm
z | 1.74 um | 1.75 um | 885 nm
Asymmetry | 0.79
Theta | 11.3°

Bead 44

Date : Mon Oct 17 13:27:47 PDT 2022
Origin : data_traditional.tif ( Nikon 40x1.15 water ) Frame size : 10 pixels

Coordinates : -2.65 um (x), 26.4 um (y), 3.4 um (z) Corresponding bead : Not found

XY profile & fitting parameters :
(red : the orignal data, green : the fit, yellow : the two merged)

Fitted on i(x,y) = A * exp(-(a*(x-xc)^2 + c*(y-yc)^2 + 2*b*(x-xc)*(y-yc))) + B R^2 = 0.945

Parameters:
A = 611.796 (brightness)
B = 129.057 (background)
a = 0.819 px
b = -0.006 px
c = 0.265 px

xc = 5.958 px
yc = 6.131 px

Z profile & fitting parameters:

Fitted on y = a + (b-a)*exp(-(x-c)^2/(2*d^2)

Sum of residuals squared: 119413.630 Standard deviation: 19.72231
R^2: 0.95518
Parameters:
a = 115.70628
b = 741.53934
c = 3.39872
d = 0.84377
FWHM | Non corrected | Corrected | Theoretical
min | 405 nm | 418 nm | 223 nm
max | 711 nm | 735 nm | 223 nm
z | 1.99 um | 1.99 um | 885 nm
Asymmetry | 0.569
Theta | -89.4°

Bead 45

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

Coordinates : 1.15 um (x), 10.2 um (y), 3.03 um (z) Corresponding bead : Not found

XY profile & fitting parameters :
(red : the orignal data, green : the fit, yellow : the two merged)

Fitted on i(x,y) = A * exp(-(a*(x-xc)^2 + c*(y-yc)^2 + 2*b*(x-xc)*(y-yc))) + B R^2 = 0.920

Parameters:
A = 601.951 (brightness)
B = 129.173 (background)
a = 0.896 px
b = -0.052 px
c = 0.320 px

xc = 6.244 px
yc = 6.508 px

Z profile & fitting parameters:

Fitted on y = a + (b-a)*exp(-(x-c)^2/(2*d^2)

Sum of residuals squared: 64408.1718 Standard deviation: 14.48443
R^2: 0.97112
Parameters:
a = 114.34080
b = 691.39492
c = 3.03073
d = 0.84452
FWHM | Non corrected | Corrected | Theoretical
min | 386 nm | 399 nm | 223 nm
max | 652 nm | 674 nm | 223 nm
z | 1.99 um | 2.0 um | 885 nm
Asymmetry | 0.592
Theta | -84.9°

Bead 46

Date : Mon Oct 17 13:27:48 PDT 2022
Origin : data_traditional.tif ( Nikon 40x1.15 water ) Frame size : 10 pixels

Coordinates : -55.7 um (x), -7.07 um (y), 3.15 um (z) Corresponding bead : Not found

XY profile & fitting parameters :
(red : the orignal data, green : the fit, yellow : the two merged)

Fitted on i(x,y) = A * exp(-(a*(x-xc)^2 + c*(y-yc)^2 + 2*b*(x-xc)*(y-yc))) + B R^2 = 0.930

Parameters:
A = 609.614 (brightness)
B = 133.078 (background)
a = 0.638 px
b = 0.117 px
c = 0.469 px

xc = 5.772 px
yc = 5.127 px

Z profile & fitting parameters:

Fitted on y = a + (b-a)*exp(-(x-c)^2/(2*d^2)

Sum of residuals squared: 123819.286 Standard deviation: 20.08283
R^2: 0.94152
Parameters:
a = 113.33539
b = 640.90655
c = 3.14607
d = 0.93462
FWHM | Non corrected | Corrected | Theoretical
min | 439 nm | 453 nm | 223 nm
max | 573 nm | 592 nm | 223 nm
z | 2.2 um | 2.21 um | 885 nm
Asymmetry | 0.766
Theta | 62.9°

Bead 47

Date : Mon Oct 17 13:27:48 PDT 2022
Origin : data_traditional.tif ( Nikon 40x1.15 water ) Frame size : 10 pixels

Coordinates : -74.2 um (x), -18.7 um (y), 3.29 um (z) Corresponding bead : Not found

XY profile & fitting parameters :
(red : the orignal data, green : the fit, yellow : the two merged)

Fitted on i(x,y) = A * exp(-(a*(x-xc)^2 + c*(y-yc)^2 + 2*b*(x-xc)*(y-yc))) + B R^2 = 0.919

Parameters:
A = 545.698 (brightness)
B = 131.157 (background)
a = 0.657 px
b = 0.066 px
c = 0.612 px

xc = 5.841 px
yc = 6.190 px

Z profile & fitting parameters:

Fitted on y = a + (b-a)*exp(-(x-c)^2/(2*d^2)

Sum of residuals squared: 77255.6089 Standard deviation: 15.86338
R^2: 0.94401
Parameters:
a = 113.69892
b = 557.05787
c = 3.28811
d = 0.86130
FWHM | Non corrected | Corrected | Theoretical
min | 437 nm | 451 nm | 223 nm
max | 487 nm | 504 nm | 223 nm
z | 2.03 um | 2.04 um | 885 nm
Asymmetry | 0.896
Theta | 54.4°

Bead 48 (Rejected)

Date : Mon Oct 17 13:27:48 PDT 2022
Origin : data_traditional.tif ( Nikon 40x1.15 water ) Frame size : 10 pixels

Coordinates : -86.2 um (x), -36.7 um (y), 19.2 um (z) Corresponding bead : Not found
Reason of rejection : R or C parameter off limits.

XY profile & fitting parameters :
(red : the orignal data, green : the fit, yellow : the two merged)

Fitted on i(x,y) = A * exp(-(a*(x-xc)^2 + c*(y-yc)^2 + 2*b*(x-xc)*(y-yc))) + B R^2 = 0.955

Parameters:
A = 969.168 (brightness)
B = 134.118 (background)
a = 0.717 px
b = 0.148 px
c = 0.621 px
xc = 7.278 px
yc = 5.917 px

Z profile & fitting parameters:

Fitted on y = a + (b-a)*exp(-(x-c)^2/(2*d^2)

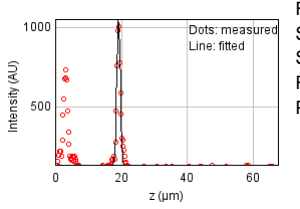
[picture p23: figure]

Sum of residuals squared: 1987325.42 Standard deviation: 80.45727
R^2: 0.64493
Parameters:
a = 133.25594
b = 1057.11556
c = 19.19684
d = 0.54019
FWHM | Non corrected | Corrected | Theoretical
min | 403 nm | 417 nm | 223 nm
max | 511 nm | 529 nm | 223 nm
z | 1.27 um | 1.28 um | 885 nm
Asymmetry | 0.789
Theta | 53.9°

Bead 49 (Rejected)

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

Coordinates : -161 um (x), -64.3 um (y), 1.62 um (z) Corresponding bead : Not found
Reason of rejection : R or C parameter off limits.

XY profile & fitting parameters :
(red : the orignal data, green : the fit, yellow : the two merged)

Fitted on i(x,y) = A * exp(-(a*(x-xc)^2 + c*(y-yc)^2 + 2*b*(x-xc)*(y-yc))) + B R^2 = 0.916

Parameters:
A = 117.864 (brightness)
B = 113.487 (background)
a = 0.332 px
b = 0.422 px
c = 0.585 px
xc = 5.960 px
yc = 5.422 px

Z profile & fitting parameters:

Fitted on y = a + (b-a)*exp(-(x-c)^2/(2*d^2)

Sum of residuals squared: 16990.4577 Standard deviation: 7.43932
R^2: 0.77611
Parameters:
a = 110.91388
b = 193.24852
c = 1.62370
d = 1.15924
FWHM | Non corrected | Corrected | Theoretical
min | 386 nm | 399 nm | 223 nm
max | 2.7 um | 2.79 um | 223 nm
z | 2.73 um | 2.74 um | 885 nm
Asymmetry | 0.143
Theta | 36.7°

Bead 50

Date : Mon Oct 17 13:27:49 PDT 2022
Origin : data_traditional.tif ( Nikon 40x1.15 water ) Frame size : 10 pixels

Coordinates : -113 um (x), 86.8 um (y), 2.6 um (z) Corresponding bead : Not found

XY profile & fitting parameters :
(red : the orignal data, green : the fit, yellow : the two merged)

Fitted on i(x,y) = A * exp(-(a*(x-xc)^2 + c*(y-yc)^2 + 2*b*(x-xc)*(y-yc))) + B R^2 = 0.905

Parameters:
A = 398.355 (brightness)
B = 125.816 (background)
a = 0.459 px
b = -0.037 px
c = 0.731 px

xc = 5.592 px
yc = 5.430 px

Z profile & fitting parameters:

Fitted on y = a + (b-a)*exp(-(x-c)^2/(2*d^2)

Sum of residuals squared: 29617.2409 Standard deviation: 9.82207
R^2: 0.97033
Parameters:
a = 112.46749
b = 471.32005
c = 2.59779
d = 0.98387
FWHM | Non corrected | Corrected | Theoretical
min | 427 nm | 441 nm | 223 nm
max | 544 nm | 562 nm | 223 nm
z | 2.32 um | 2.33 um | 885 nm
Asymmetry | 0.785
Theta | -7.7°

Bead 51

Date : Mon Oct 17 13:27:49 PDT 2022
Origin : data_traditional.tif ( Nikon 40x1.15 water ) Frame size : 10 pixels

Coordinates : 58.0 um (x), 43.1 um (y), 3.38 um (z) Corresponding bead : Not found

XY profile & fitting parameters :
(red : the orignal data, green : the fit, yellow : the two merged)

Fitted on i(x,y) = A * exp(-(a*(x-xc)^2 + c*(y-yc)^2 + 2*b*(x-xc)*(y-yc))) + B R^2 = 0.968

Parameters:
A = 673.344 (brightness)
B = 121.548 (background)
a = 0.489 px
b = -0.237 px
c = 0.638 px

xc = 6.786 px
yc = 6.891 px

Z profile & fitting parameters:

Fitted on y = a + (b-a)*exp(-(x-c)^2/(2*d^2)

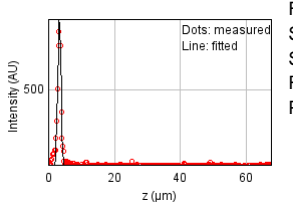
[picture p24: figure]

Sum of residuals squared: 56826.5603 Standard deviation: 13.60525
R^2: 0.97397
Parameters:
a = 114.40176
b = 870.76746
c = 3.37836
d = 0.47300
FWHM | Non corrected | Corrected | Theoretical
min | 407 nm | 420 nm | 223 nm
max | 653 nm | 675 nm | 223 nm
z | 1.11 um | 1.12 um | 885 nm
Asymmetry | 0.623
Theta | -36.3°

Bead 52 (Rejected)

Date : Mon Oct 17 13:27:49 PDT 2022
Origin : data_traditional.tif ( Nikon 40x1.15 water ) Frame size : 10 pixels

Coordinates : 107 um (x), 31.6 um (y), 1.66 um (z) Corresponding bead : Not found
Reason of rejection : R or C parameter off limits.

XY profile & fitting parameters :
(red : the orignal data, green : the fit, yellow : the two merged)

Fitted on i(x,y) = A * exp(-(a*(x-xc)^2 + c*(y-yc)^2 + 2*b*(x-xc)*(y-yc))) + B R^2 = 0.806

Parameters:
A = 79.091 (brightness)
B = 115.148 (background)
a = 0.166 px
b = 0.002 px
c = 0.246 px
xc = 6.244 px
yc = 6.514 px

Z profile & fitting parameters:

Fitted on y = a + (b-a)*exp(-(x-c)^2/(2*d^2)

Sum of residuals squared: 19505.2404 Standard deviation: 7.97088
R^2: 0.91901
Parameters:
a = 111.06873
b = 278.10892
c = -0.073302
d = 2.03966
FWHM | Non corrected | Corrected | Theoretical
min | 738 nm | 763 nm | 223 nm
max | 899 nm | 930 nm | 223 nm
z | 4.8 um | 4.82 um | 885 nm
Asymmetry | 0.82
Theta | 1.6°

Bead 53

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

Coordinates : 10.5 um (x), 25.8 um (y), 12.4 um (z) Corresponding bead : Not found

XY profile & fitting parameters :
(red : the orignal data, green : the fit, yellow : the two merged)

Fitted on i(x,y) = A * exp(-(a*(x-xc)^2 + c*(y-yc)^2 + 2*b*(x-xc)*(y-yc))) + B R^2 = 0.975

Parameters:
A = 607.575 (brightness)
B = 120.865 (background)
a = 0.687 px
b = -0.068 px
c = 0.463 px

xc = 1.581 px
yc = 6.613 px

Z profile & fitting parameters:

Fitted on y = a + (b-a)*exp(-(x-c)^2/(2*d^2)

Sum of residuals squared: 93398.1120 Standard deviation: 17.44214
R^2: 0.94545
Parameters:
a = 118.18877
b = 652.60416
c = 12.39378
d = 0.73146
FWHM | Non corrected | Corrected | Theoretical
min | 436 nm | 451 nm | 223 nm
max | 550 nm | 568 nm | 223 nm
z | 1.72 um | 1.73 um | 885 nm
Asymmetry | 0.793
Theta | -74.3°

Bead 54 (Rejected)

Date : Mon Oct 17 13:27:50 PDT 2022
Origin : data_traditional.tif ( Nikon 40x1.15 water ) Frame size : 10 pixels

Coordinates : -41.6 um (x), 26.1 um (y), 2.54 um (z)
Corresponding bead : Not found
Reason of rejection : The fitted bead is likely to be a different bead from the center bead.

XY profile & fitting parameters :
(red : the orignal data, green : the fit, yellow : the two merged)

Fitted on i(x,y) = A * exp(-(a*(x-xc)^2 + c*(y-yc)^2 + 2*b*(x-xc)*(y-yc))) + B R^2 = 0.822

Parameters:
A = 437.531 (brightness)
B = 134.702 (background)
a = 0.476 px
b = 0.050 px
c = 0.214 px
xc = 4.985 px
yc = 5.441 px

Z profile & fitting parameters:

Fitted on y = a + (b-a)*exp(-(x-c)^2/(2*d^2)

Sum of residuals squared: 19934.1228 Standard deviation: 8.05804
R^2: 0.71111
Parameters:
a = 113.76921
b = 178.89968
c = 2.53544
d = 1.56566
FWHM | Non corrected | Corrected | Theoretical
min | 526 nm | 544 nm | 223 nm
max | 809 nm | 836 nm | 223 nm
z | 3.69 um | 3.7 um | 885 nm
Asymmetry | 0.65
Theta | 79.5°

Bead 55

Date : Mon Oct 17 13:27:50 PDT 2022
Origin : data_traditional.tif ( Nikon 40x1.15 water ) Frame size : 10 pixels

Coordinates : -63.9 um (x), 11.0 um (y), 3.86 um (z) Corresponding bead : Not found

XY profile & fitting parameters :
(red : the orignal data, green : the fit, yellow : the two merged)

Fitted on i(x,y) = A * exp(-(a*(x-xc)^2 + c*(y-yc)^2 + 2*b*(x-xc)*(y-yc))) + B R^2 = 0.955

Parameters:
A = 743.107 (brightness)
B = 124.182 (background)
a = 0.648 px
b = 0.165 px
c = 0.605 px

xc = 5.469 px
yc = 7.015 px

Z profile & fitting parameters:

Fitted on y = a + (b-a)*exp(-(x-c)^2/(2*d^2)

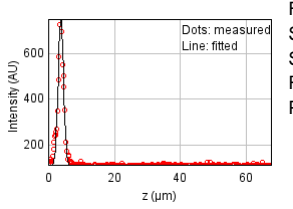
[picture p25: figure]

Sum of residuals squared: 61075.9252 Standard deviation: 14.10476
R^2: 0.97646
Parameters:
a = 113.49878
b = 750.97695
c = 3.86101
d = 0.80781
FWHM | Non corrected | Corrected | Theoretical
min | 411 nm | 425 nm | 223 nm
max | 540 nm | 558 nm | 223 nm
z | 1.9 um | 1.91 um | 885 nm
Asymmetry | 0.762
Theta | 48.7°

Bead 56 (Rejected)

Date : Mon Oct 17 13:27:50 PDT 2022
Origin : data_traditional.tif ( Nikon 40x1.15 water ) Frame size : 10 pixels

Coordinates : -134 um (x), -22.1 um (y), 1.81 um (z) Corresponding bead : Not found
Reason of rejection : R or C parameter off limits.

XY profile & fitting parameters :
(red : the orignal data, green : the fit, yellow : the two merged)

Fitted on i(x,y) = A * exp(-(a*(x-xc)^2 + c*(y-yc)^2 + 2*b*(x-xc)*(y-yc))) + B R^2 = 0.851

Parameters:
A = 133.211 (brightness)
B = 113.133 (background)
a = 0.298 px
b = 0.239 px
c = 0.478 px
xc = 5.219 px
yc = 6.501 px

Z profile & fitting parameters:

Fitted on y = a + (b-a)*exp(-(x-c)^2/(2*d^2)

Sum of residuals squared: 31983.0434 Standard deviation: 10.20683
R^2: 0.74654
Parameters:
a = 113.99985
b = 226.06912
c = 1.80964
d = 0.98160
FWHM | Non corrected | Corrected | Theoretical
min | 457 nm | 472 nm | 223 nm
max | 1.01 um | 1.04 um | 223 nm
z | 2.31 um | 2.32 um | 885 nm
Asymmetry | 0.454
Theta | 34.7°

Bead 57 (Rejected)

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

Coordinates : 101 um (x), -22.7 um (y), 2.96 um (z) Corresponding bead : Not found
Reason of rejection : R or C parameter off limits.

XY profile & fitting parameters :
(red : the orignal data, green : the fit, yellow : the two merged)

Fitted on i(x,y) = A * exp(-(a*(x-xc)^2 + c*(y-yc)^2 + 2*b*(x-xc)*(y-yc))) + B R^2 = 0.844

Parameters:
A = 110.101 (brightness)
B = 119.186 (background)
a = 0.215 px
b = -0.070 px
c = 0.240 px
xc = 5.215 px
yc = 6.271 px

Z profile & fitting parameters:

Fitted on y = a + (b-a)*exp(-(x-c)^2/(2*d^2)

Sum of residuals squared: 15622.8391 Standard deviation: 7.13363
R^2: 0.86563
Parameters:
a = 111.53663
b = 216.15980
c = 2.95653
d = 1.21826
FWHM | Non corrected | Corrected | Theoretical
min | 670 nm | 693 nm | 223 nm
max | 926 nm | 958 nm | 223 nm
z | 2.87 um | 2.88 um | 885 nm
Asymmetry | 0.723
Theta | -39.8°

Bead 58 (Rejected)

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

Coordinates : -44.7 um (x), -46.8 um (y), 1.4 um (z)
Corresponding bead : Not found
Reason of rejection : The fitted bead is likely to be a different bead from the center bead.

XY profile & fitting parameters :
(red : the orignal data, green : the fit, yellow : the two merged)

Fitted on i(x,y) = A * exp(-(a*(x-xc)^2 + c*(y-yc)^2 + 2*b*(x-xc)*(y-yc))) + B R^2 = 0.866

Parameters:
A = 220.823 (brightness)
B = 121.905 (background)
a = 0.149 px
b = -0.136 px
c = 0.606 px
xc = 2.745 px
yc = 4.594 px

Z profile & fitting parameters:

Fitted on y = a + (b-a)*exp(-(x-c)^2/(2*d^2)

Sum of residuals squared: 16463.3228 Standard deviation: 7.32301
R^2: 0.81172
Parameters:
a = 113.06793
b = 212.87492
c = 1.40334
d = 0.93557
FWHM | Non corrected | Corrected | Theoretical
min | 457 nm | 472 nm | 223 nm
max | 1.09 um | 1.13 um | 223 nm
z | 2.2 um | 2.21 um | 885 nm
Asymmetry | 0.417
Theta | -15.3°

Bead 59

Date : Mon Oct 17 13:27:51 PDT 2022
Origin : data_traditional.tif ( Nikon 40x1.15 water ) Frame size : 10 pixels

Coordinates : -28.4 um (x), -52.9 um (y), 49.5 um (z) Corresponding bead : Not found

XY profile & fitting parameters :
(red : the orignal data, green : the fit, yellow : the two merged)

Fitted on i(x,y) = A * exp(-(a*(x-xc)^2 + c*(y-yc)^2 + 2*b*(x-xc)*(y-yc))) + B R^2 = 0.990

Parameters:
A = 1910.851 (brightness)
B = 128.682 (background)
a = 1.021 px
b = -0.019 px
c = 0.402 px

xc = 3.854 px
yc = 4.296 px

Z profile & fitting parameters:

Fitted on y = a + (b-a)*exp(-(x-c)^2/(2*d^2)

Sum of residuals squared: 223933.692 Standard deviation: 27.00788
R^2: 0.97901
Parameters:
a = 121.86963
b = 1804.23374
c = 49.52446
d = 0.46948
FWHM | Non corrected | Corrected | Theoretical
min | 362 nm | 375 nm | 223 nm
max | 578 nm | 598 nm | 223 nm
z | 1.11 um | 1.11 um | 885 nm
Asymmetry | 0.627
Theta | -88.2°

Bead 60 (Rejected)

Date : Mon Oct 17 13:27:51 PDT 2022
Origin : data_traditional.tif ( Nikon 40x1.15 water ) Frame size : 10 pixels

Coordinates : 62.1 um (x), -68.2 um (y), 850 nm (z) Corresponding bead : Not found
Reason of rejection : R or C parameter off limits.

XY profile & fitting parameters :
(red : the orignal data, green : the fit, yellow : the two merged)

Fitted on i(x,y) = A * exp(-(a*(x-xc)^2 + c*(y-yc)^2 + 2*b*(x-xc)*(y-yc))) + B R^2 = 0.853

Parameters:
A = 88.893 (brightness)
B = 123.945 (background)
a = 0.188 px
b = 0.190 px
c = 0.341 px
xc = 5.224 px
yc = 5.920 px

Z profile & fitting parameters:

Fitted on y = a + (b-a)*exp(-(x-c)^2/(2*d^2)


Sum of residuals squared: 16206.1904 Standard deviation: 7.26560
R^2: 0.83444
Parameters:
a = 112.86981
b = 216.21497
c = 0.85010
d = 1.11526
FWHM | Non corrected | Corrected | Theoretical
min | 535 nm | 553 nm | 223 nm
max | 1.49 um | 1.55 um | 223 nm
z | 2.63 um | 2.64 um | 885 nm
Asymmetry | 0.358
Theta | 34.0°

Bead 61

Date : Mon Oct 17 13:27:51 PDT 2022
Origin : data_traditional.tif ( Nikon 40x1.15 water ) Frame size : 10 pixels

Coordinates : -128 um (x), 88.7 um (y), 2.99 um (z) Corresponding bead : Not found

XY profile & fitting parameters :
(red : the orignal data, green : the fit, yellow : the two merged)

Fitted on i(x,y) = A * exp(-(a*(x-xc)^2 + c*(y-yc)^2 + 2*b*(x-xc)*(y-yc))) + B R^2 = 0.928

Parameters:
A = 455.216 (brightness)
B = 124.700 (background)
a = 0.319 px
b = -0.219 px
c = 0.717 px

xc = 6.223 px
yc = 6.019 px

Z profile & fitting parameters:

Fitted on y = a + (b-a)*exp(-(x-c)^2/(2*d^2)

Sum of residuals squared: 67460.9654 Standard deviation: 14.82372
R^2: 0.93910
Parameters:
a = 114.30041
b = 536.39756
c = 2.99052
d = 0.75449
FWHM | Non corrected | Corrected | Theoretical
min | 406 nm | 420 nm | 223 nm
max | 778 nm | 804 nm | 223 nm
z | 1.78 um | 1.78 um | 885 nm
Asymmetry | 0.522
Theta | -23.9°

Bead 62

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

Coordinates : 131 um (x), 82.2 um (y), 2.28 um (z) Corresponding bead : Not found

XY profile & fitting parameters :
(red : the orignal data, green : the fit, yellow : the two merged)

Fitted on i(x,y) = A * exp(-(a*(x-xc)^2 + c*(y-yc)^2 + 2*b*(x-xc)*(y-yc))) + B R^2 = 0.950

Parameters:
A = 174.059 (brightness)
B = 115.418 (background)
a = 0.080 px
b = 0.088 px
c = 0.861 px

xc = 5.440 px
yc = 5.181 px

Z profile & fitting parameters:

Fitted on y = a + (b-a)*exp(-(x-c)^2/(2*d^2)

Sum of residuals squared: 21021.2902 Standard deviation: 8.27486
R^2: 0.88109
Parameters:
a = 110.14588
b = 242.29003
c = 2.28180
d = 1.17930
FWHM | Non corrected | Corrected | Theoretical
min | 393 nm | 406 nm | 223 nm
max | 1.38 um | 1.43 um | 223 nm
z | 2.78 um | 2.79 um | 885 nm
Asymmetry | 0.284
Theta | 6.3°

Bead 63

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

Coordinates : -60.5 um (x), 60.6 um (y), 2.88 um (z) Corresponding bead : Not found

XY profile & fitting parameters :
(red : the orignal data, green : the fit, yellow : the two merged)

Fitted on i(x,y) = A * exp(-(a*(x-xc)^2 + c*(y-yc)^2 + 2*b*(x-xc)*(y-yc))) + B R^2 = 0.917

Parameters:
A = 232.590 (brightness)
B = 117.618 (background)
a = 0.390 px
b = -0.002 px
c = 0.218 px

xc = 6.110 px
yc = 6.584 px

Z profile & fitting parameters:

Fitted on y = a + (b-a)*exp(-(x-c)^2/(2*d^2)


Sum of residuals squared: 22042.4013 Standard deviation: 8.47345
R^2: 0.93909
Parameters:
a = 113.07224
b = 361.11215
c = 2.88204
d = 0.71221
FWHM | Non corrected | Corrected | Theoretical
min | 586 nm | 606 nm | 223 nm
max | 785 nm | 811 nm | 223 nm
z | 1.68 um | 1.68 um | 885 nm
Asymmetry | 0.747
Theta | -89.3°

Bead 64 (Rejected)

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

Coordinates : -88.2 um (x), 32.8 um (y), 61.2 um (z) Corresponding bead : Not found
Reason of rejection : R or C parameter off limits.

XY profile & fitting parameters :
(red : the orignal data, green : the fit, yellow : the two merged)

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

Fitted on y = a + (b-a)*exp(-(x-c)^2/(2*d^2)

Sum of residuals squared: 244303.132 Standard deviation: 28.20950
R^2: 0.98238
Parameters:
a = 121.14765
b = 2069.70767
c = 61.19044
d = 0.45608
FWHM | Non corrected | Corrected | Theoretical
min | 0 | 0 | 223 nm
max | 0 | 0 | 223 nm
z | 1.07 um | 1.08 um | 885 nm
Asymmetry | 0.0
Theta | 0.0°

Bead 65 (Rejected)

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

Coordinates : 48.0 um (x), 8.07 um (y), 1.53 um (z)
Corresponding bead : Not found
Reason of rejection : The fitted bead is likely to be a different bead from the center bead.

XY profile & fitting parameters :
(red : the orignal data, green : the fit, yellow : the two merged)

Fitted on i(x,y) = A * exp(-(a*(x-xc)^2 + c*(y-yc)^2 + 2*b*(x-xc)*(y-yc))) + B R^2 = 0.833

Parameters:
A = 363.632 (brightness)
B = 143.362 (background)
a = 0.157 px
b = -0.006 px
c = 0.180 px
xc = -0.013 px
yc = 3.310 px

Z profile & fitting parameters:

Fitted on y = a + (b-a)*exp(-(x-c)^2/(2*d^2)

Sum of residuals squared: 16769.2282 Standard deviation: 7.39073
R^2: 0.67143
Parameters:
a = 114.02661
b = 208.40480
c = 1.52983
d = 0.49008
FWHM | Non corrected | Corrected | Theoretical
min | 861 nm | 890 nm | 223 nm
max | 928 nm | 960 nm | 223 nm
z | 1.15 um | 1.16 um | 885 nm
Asymmetry | 0.927
Theta | -13.6°

Bead 66 (Rejected)

Date : Mon Oct 17 13:27:52 PDT 2022
Origin : data_traditional.tif ( Nikon 40x1.15 water ) Frame size : 10 pixels

Coordinates : 47.5 um (x), -7.4 um (y), 1.83 um (z)
Corresponding bead : Not found
Reason of rejection : The fitted bead is likely to be a different bead from the center bead.

XY profile & fitting parameters :
(red : the orignal data, green : the fit, yellow : the two merged)

Fitted on i(x,y) = A * exp(-(a*(x-xc)^2 + c*(y-yc)^2 + 2*b*(x-xc)*(y-yc))) + B R^2 = 0.709

Parameters:
A = 132.423 (brightness)
B = 90.189 (background)
a = 0.049 px
b = 0.000 px
c = 0.023 px
xc = 4.939 px
yc = 2.658 px

Z profile & fitting parameters:

Fitted on y = a + (b-a)*exp(-(x-c)^2/(2*d^2)

Sum of residuals squared: 15735.4398 Standard deviation: 7.15929
R^2: 0.72754
Parameters:
a = 114.13592
b = 204.61002
c = 1.83048
d = 0.65985
FWHM | Non corrected | Corrected | Theoretical
min | 1.65 um | 1.71 um | 223 nm
max | 2.4 um | 2.48 um | 223 nm
z | 1.55 um | 1.56 um | 885 nm
Asymmetry | 0.689
Theta | 89.3°

Bead 67 (Rejected)

Date : Mon Oct 17 13:27:52 PDT 2022
Origin : data_traditional.tif ( Nikon 40x1.15 water ) Frame size : 10 pixels

Coordinates : -49.5 um (x), -83.8 um (y), 1.44 um (z) Corresponding bead : Not found
Reason of rejection : R or C parameter off limits.

XY profile & fitting parameters :
(red : the orignal data, green : the fit, yellow : the two merged)

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

Fitted on y = a + (b-a)*exp(-(x-c)^2/(2*d^2)

Sum of residuals squared: 12272.3861 Standard deviation: 6.32259
R^2: 0.83273
Parameters:
a = 113.08450
b = 225.28894
c = 1.44265
d = 0.62249
FWHM | Non corrected | Corrected | Theoretical
min | 0 | 0 | 223 nm
max | 0 | 0 | 223 nm
z | 1.47 um | 1.47 um | 885 nm
Asymmetry | 0.0
Theta | 0.0°

Bead 68 (Rejected)

Date : Mon Oct 17 13:27:52 PDT 2022
Origin : data_traditional.tif ( Nikon 40x1.15 water ) Frame size : 10 pixels

Coordinates : -74.7 um (x), -95.2 um (y), 1.31 um (z) Corresponding bead : Not found
Reason of rejection : R or C parameter off limits.

XY profile & fitting parameters :
(red : the orignal data, green : the fit, yellow : the two merged)

Fitted on i(x,y) = A * exp(-(a*(x-xc)^2 + c*(y-yc)^2 + 2*b*(x-xc)*(y-yc))) + B R^2 = 0.855

Parameters:
A = 86.964 (brightness)
B = 121.222 (background)
a = 0.073 px
b = -0.119 px
c = 0.491 px
xc = 5.231 px
yc = 5.629 px

Z profile & fitting parameters:

Fitted on y = a + (b-a)*exp(-(x-c)^2/(2*d^2)

Sum of residuals squared: 16288.5348 Standard deviation: 7.28403
R^2: 0.82646
Parameters:
a = 112.14377
b = 204.97950
c = 1.30800
d = 1.24520
FWHM | Non corrected | Corrected | Theoretical
min | 507 nm | 524 nm | 223 nm
max | 1.8 um | 1.86 um | 223 nm
z | 2.93 um | 2.94 um | 885 nm
Asymmetry | 0.281
Theta | -14.8°

Bead 69 (Rejected)

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

Coordinates : 91.3 um (x), 68.1 um (y), 2.0 um (z)
Corresponding bead : Not found
Reason of rejection : The fitted bead is likely to be a different bead from the center bead.

XY profile & fitting parameters :
(red : the orignal data, green : the fit, yellow : the two merged)

Fitted on i(x,y) = A * exp(-(a*(x-xc)^2 + c*(y-yc)^2 + 2*b*(x-xc)*(y-yc))) + B R^2 = 0.902

Parameters:
A = 119.088 (brightness)
B = 115.353 (background)
a = 0.068 px
b = 0.084 px
c = 0.290 px
xc = 2.998 px
yc = 7.309 px

Z profile & fitting parameters:

Fitted on y = a + (b-a)*exp(-(x-c)^2/(2*d^2)


Sum of residuals squared: 13094.6316 Standard deviation: 6.53097
R^2: 0.68080
Parameters:
a = 113.54192
b = 204.13000
c = 2.00113
d = 0.43220
FWHM | Non corrected | Corrected | Theoretical
min | 650 nm | 672 nm | 223 nm
max | 1.84 um | 1.9 um | 223 nm
z | 1.02 um | 1.02 um | 885 nm
Asymmetry | 0.353
Theta | 18.5°

Bead 70 (Rejected)

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

Coordinates : 91.3 um (x), 68.1 um (y), 2.0 um (z)
Corresponding bead : Not found
Reason of rejection : The fitted bead is likely to be a different bead from the center bead.

XY profile & fitting parameters :
(red : the orignal data, green : the fit, yellow : the two merged)

Fitted on i(x,y) = A * exp(-(a*(x-xc)^2 + c*(y-yc)^2 + 2*b*(x-xc)*(y-yc))) + B R^2 = 0.785
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

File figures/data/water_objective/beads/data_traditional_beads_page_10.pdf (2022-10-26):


Bead 901

Date : Mon Oct 17 13:28:39 PDT 2022
Origin : data_traditional.tif ( Nikon 40x1.15 water ) Frame size : 10 pixels

Coordinates : -99.4 um (x), -44.9 um (y), 19.2 um (z) Corresponding bead : Not found

XY profile & fitting parameters :
(red : the orignal data, green : the fit, yellow : the two merged)

Fitted on i(x,y) = A * exp(-(a*(x-xc)^2 + c*(y-yc)^2 + 2*b*(x-xc)*(y-yc))) + B R^2 = 0.973

Parameters:
A = 956.967 (brightness)
B = 128.920 (background)
a = 0.693 px
b = 0.132 px
c = 0.500 px
xc = 5.045 px
yc = 5.152 px

Z profile & fitting parameters:

Fitted on y = a + (b-a)*exp(-(x-c)^2/(2*d^2) Sum of residuals squared: 82058.0284 Standard deviation: 16.34901
R^2: 0.97772
Parameters:
a = 113.11923
b = 998.67274
c = 19.18387
d = 0.58805
FWHM | Non corrected | Corrected | Theoretical
min | 420 nm | 434 nm | 223 nm
max | 557 nm | 576 nm | 223 nm
z | 1.38 um | 1.39 um | 885 nm
Asymmetry | 0.755
Theta | 63.1°

Bead 902

Date : Mon Oct 17 13:28:39 PDT 2022
Origin : data_traditional.tif ( Nikon 40x1.15 water ) Frame size : 10 pixels

Coordinates : -37.4 um (x), -57.7 um (y), 24.8 um (z) Corresponding bead : Not found

XY profile & fitting parameters :
(red : the orignal data, green : the fit, yellow : the two merged)

Fitted on i(x,y) = A * exp(-(a*(x-xc)^2 + c*(y-yc)^2 + 2*b*(x-xc)*(y-yc))) + B R^2 = 0.942

Parameters:
A = 1238.833 (brightness)
B = 142.862 (background)
a = 0.649 px
b = 0.030 px
c = 0.473 px
xc = 7.900 px
yc = 4.344 px

Z profile & fitting parameters:

Fitted on y = a + (b-a)*exp(-(x-c)^2/(2*d^2) Sum of residuals squared: 248654.228 Standard deviation: 28.45960
R^2: 0.96464
Parameters:
a = 118.05889
b = 1360.37902
c = 24.75373
d = 0.56214
FWHM | Non corrected | Corrected | Theoretical
min | 453 nm | 468 nm | 223 nm
max | 535 nm | 554 nm | 223 nm
z | 1.32 um | 1.33 um | 885 nm
Asymmetry | 0.846
Theta | 80.6°

Bead 903

Date : Mon Oct 17 13:28:39 PDT 2022
Origin : data_traditional.tif ( Nikon 40x1.15 water ) Frame size : 10 pixels

Coordinates : 38.1 um (x), -62.5 um (y), 19.2 um (z) Corresponding bead : Not found

XY profile & fitting parameters :
(red : the orignal data, green : the fit, yellow : the two merged)

Fitted on i(x,y) = A * exp(-(a*(x-xc)^2 + c*(y-yc)^2 + 2*b*(x-xc)*(y-yc))) + B R^2 = 0.964

Parameters:
A = 1031.041 (brightness)
B = 132.861 (background)
a = 0.798 px
b = -0.154 px
c = 0.395 px
xc = 6.135 px
yc = 4.264 px

Z profile & fitting parameters:

Fitted on y = a + (b-a)*exp(-(x-c)^2/(2*d^2) Sum of residuals squared: 36788.4105 Standard deviation: 10.94678
R^2: 0.99156
Parameters:
a = 114.54972
b = 1168.59942
c = 19.19016
d = 0.49599
FWHM | Non corrected | Corrected | Theoretical
min | 397 nm | 411 nm | 223 nm
max | 626 nm | 647 nm | 223 nm
z | 1.17 um | 1.17 um | 885 nm
Asymmetry | 0.635
Theta | -71.3°

Bead 904 (Rejected)

Date : Mon Oct 17 13:28:40 PDT 2022
Origin : data_traditional.tif ( Nikon 40x1.15 water ) Frame size : 10 pixels

Coordinates : 40.7 um (x), -80.5 um (y), 43.4 um (z) Corresponding bead : Not found
Reason of rejection : R or C parameter off limits.

XY profile & fitting parameters :
(red : the orignal data, green : the fit, yellow : the two merged)

Fitted on y = a + (b-a)*exp(-(x-c)^2/(2*d^2)

Z profile & fitting parameters:
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

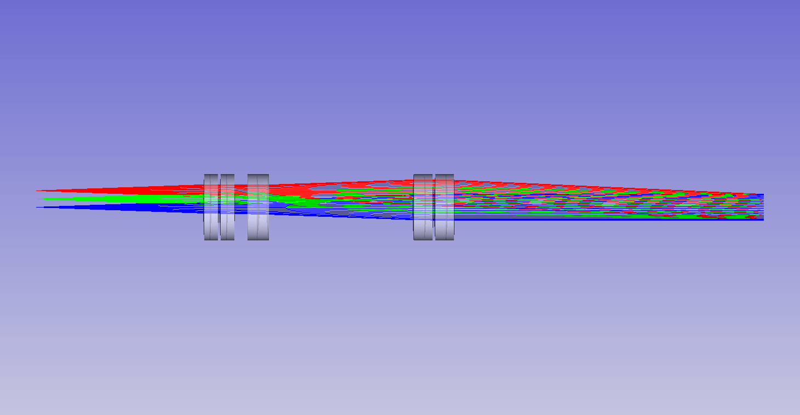
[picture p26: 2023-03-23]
figures/zoom_lens/optics/output_reversed.gif

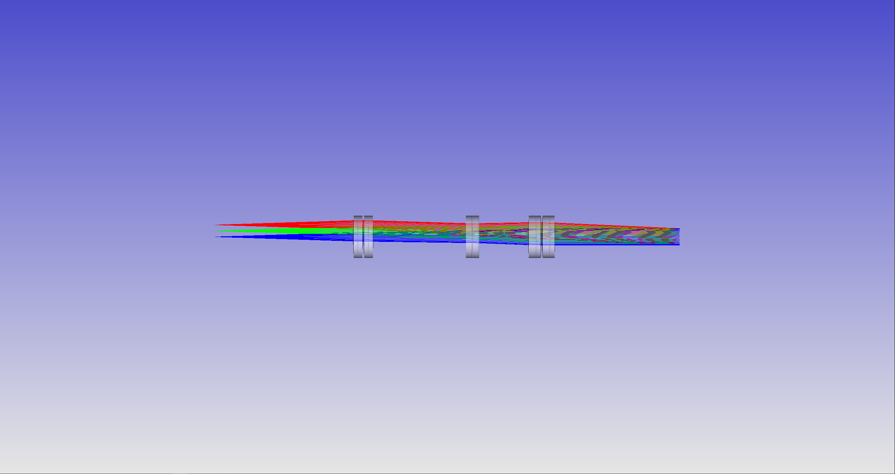
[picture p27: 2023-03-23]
figures/zoom_lens/optics/animation_images_reversed/7_reversed.png

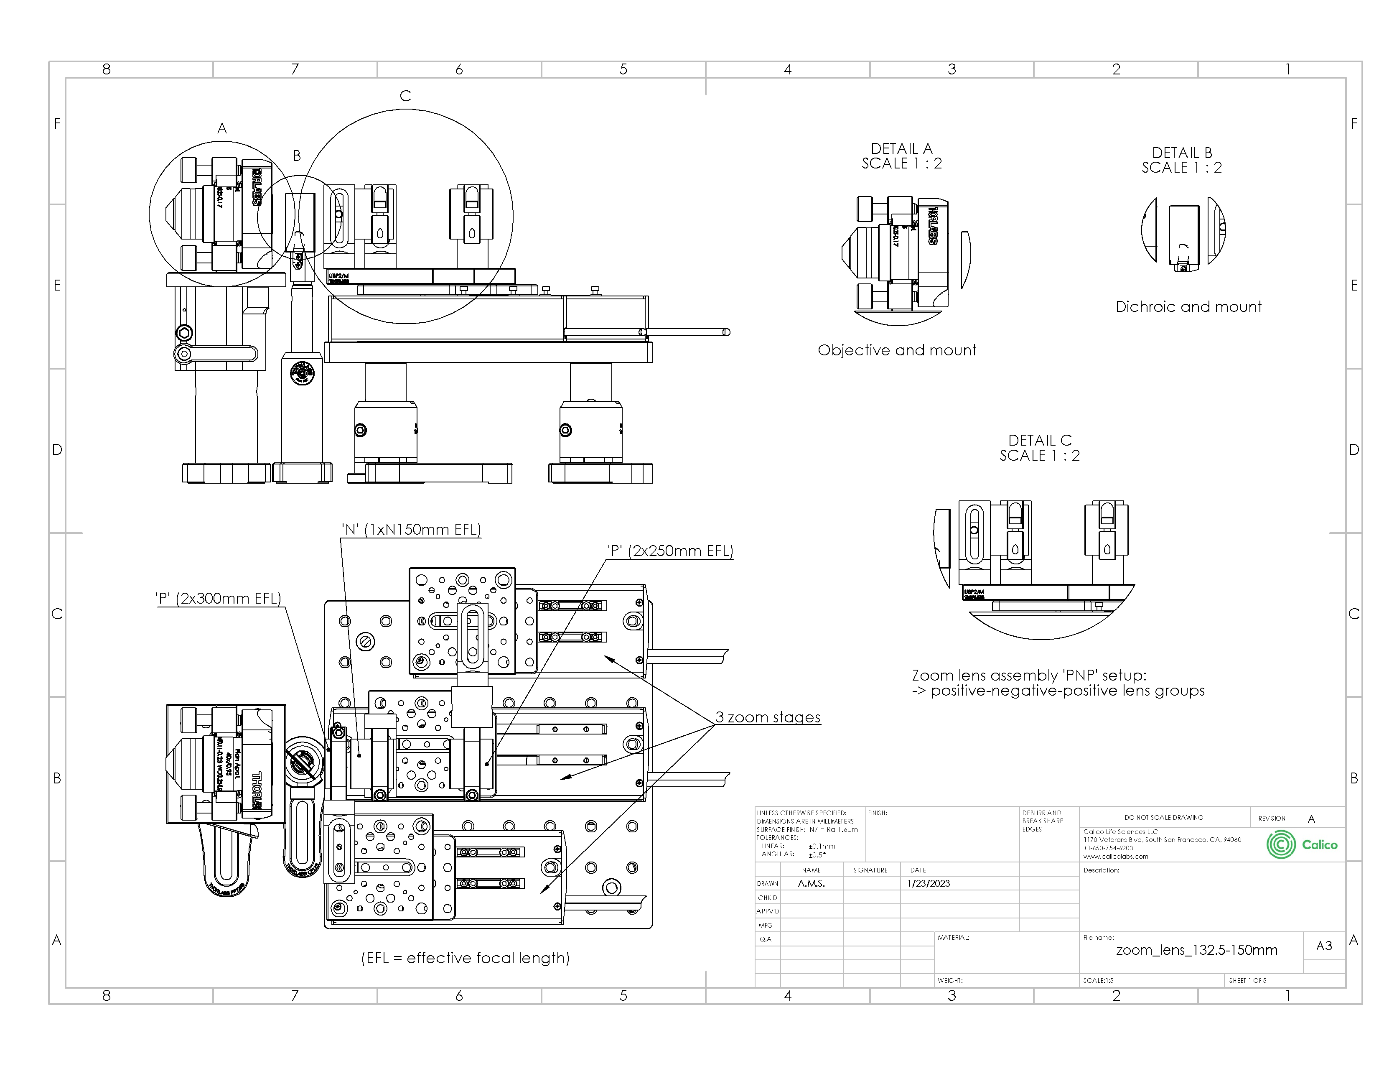
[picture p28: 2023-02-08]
figures/zoom_lens/mechanics/images/zoom_lens_132.5-150mm_sheet_1.png

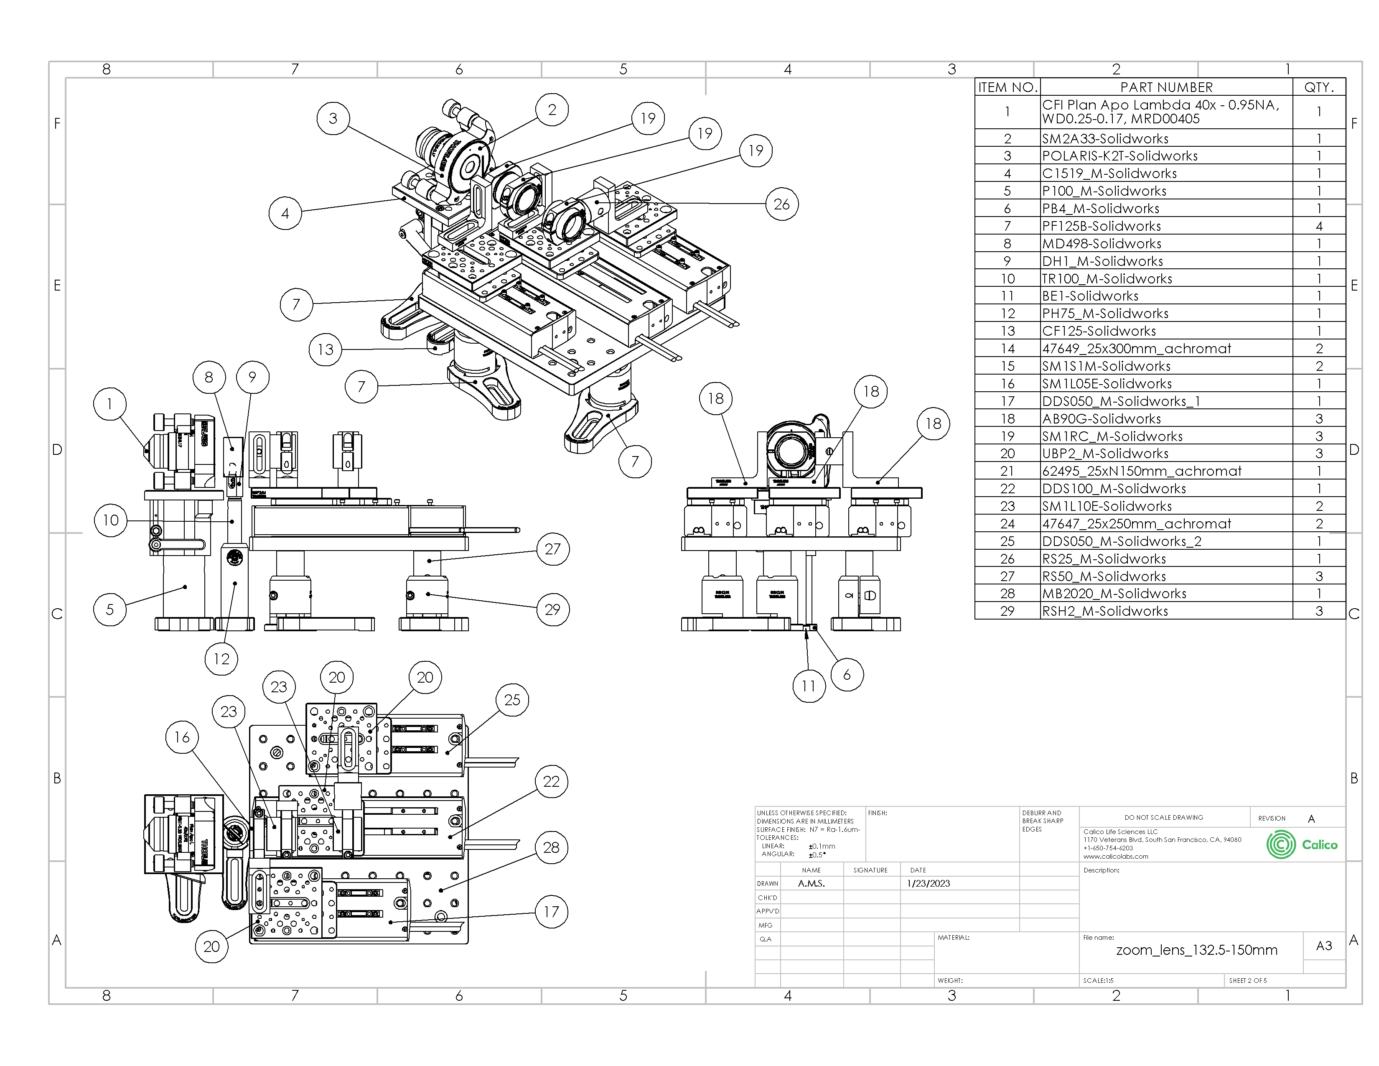
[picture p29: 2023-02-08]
figures/zoom_lens/mechanics/images/zoom_lens_132.5-150mm_sheet_2.png

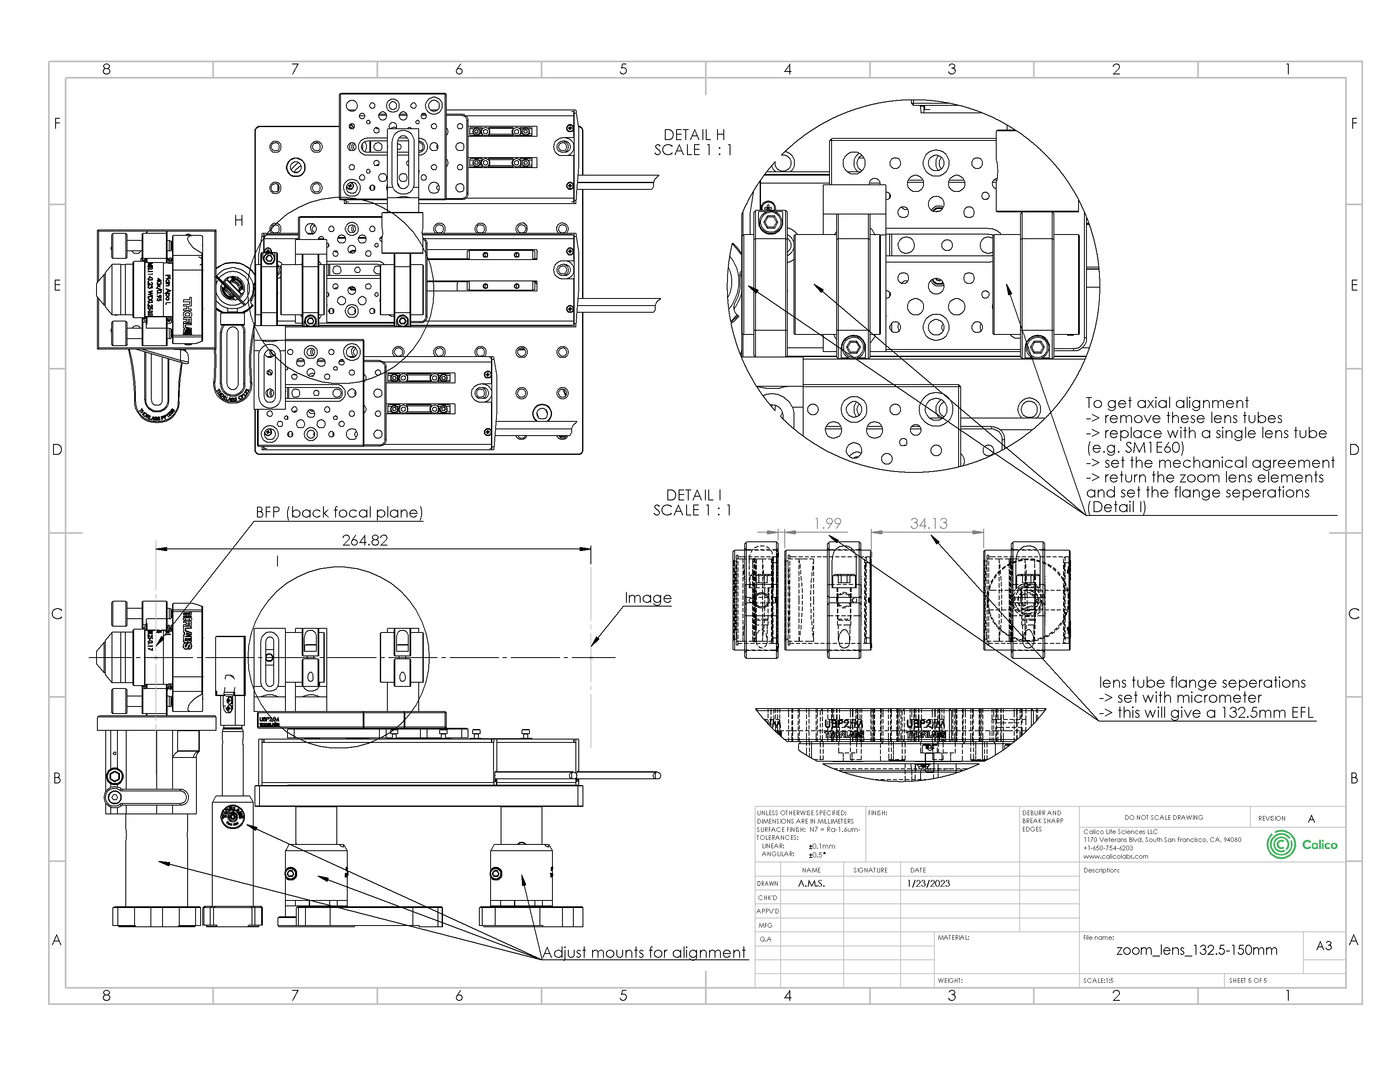
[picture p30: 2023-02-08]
figures/zoom_lens/mechanics/images/zoom_lens_132.5-150mm_sheet_5.png

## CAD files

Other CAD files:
figures/zoom_lens/mechanics/Zoom_lens_132.5-150mm.SLDDRW

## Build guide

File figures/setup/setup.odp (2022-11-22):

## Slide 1

Standard setup

Image plane

Dish sidewall

Sample (ns)

Coverslip (dish base)

WD

Immersion (ni)

Screen

Objective

Tube lens

Image

Camera

Cable

Mirror

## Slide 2

Remote refocus setup

Image plane

Remote 3D copy

Tube lens

Tube lens

Objective

Objective

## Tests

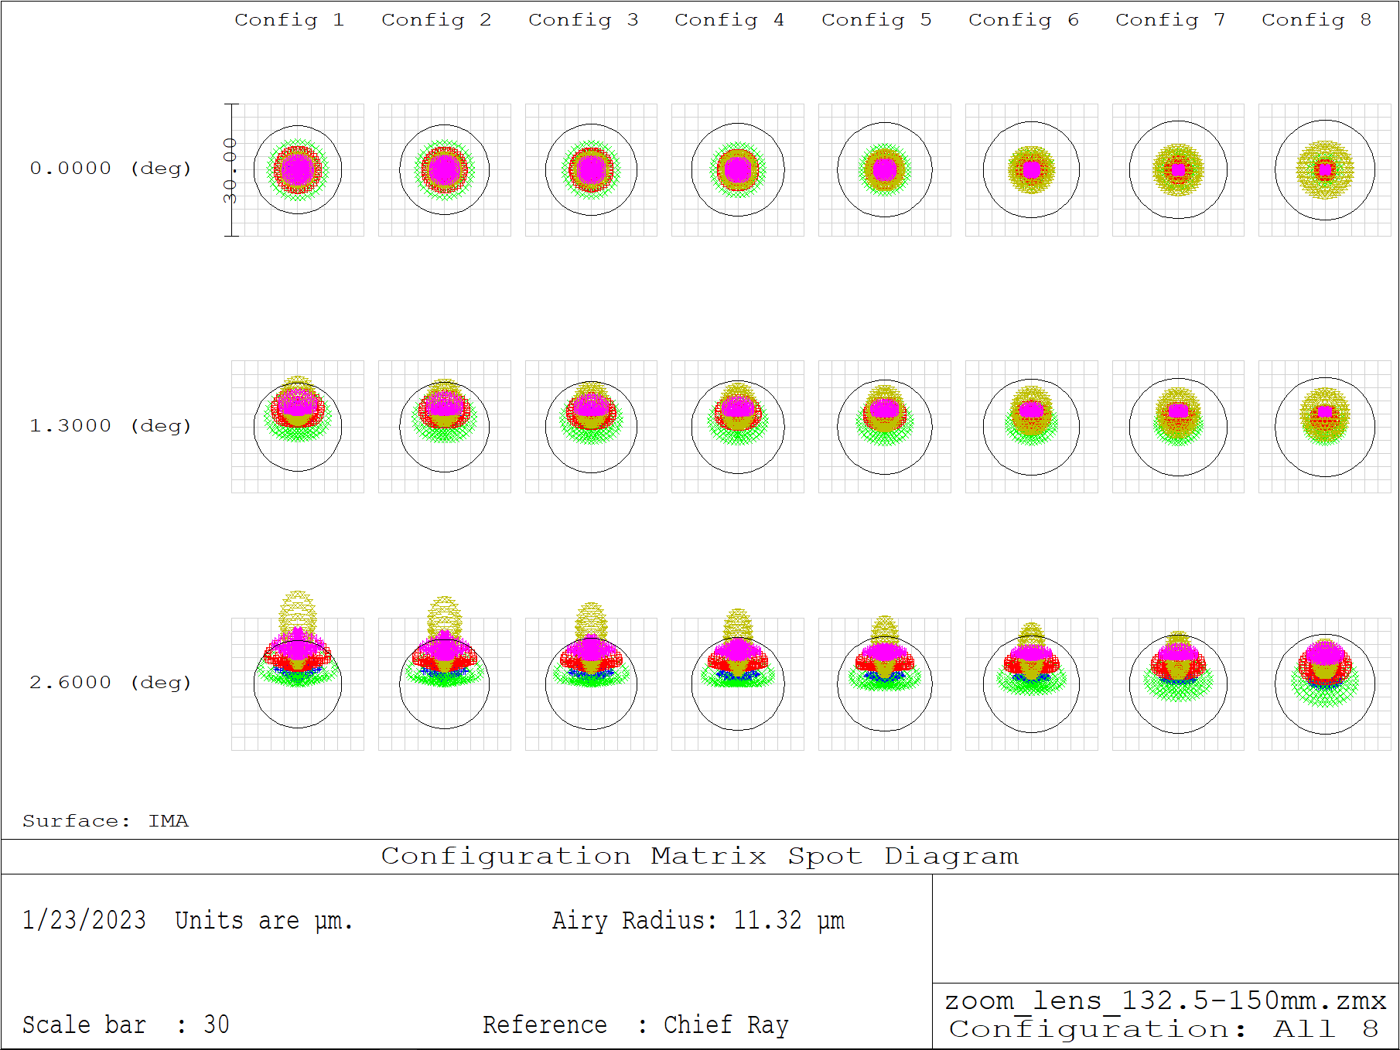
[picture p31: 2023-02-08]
figures/zoom_lens/optics/performance/spot_diagram_all_configs.png

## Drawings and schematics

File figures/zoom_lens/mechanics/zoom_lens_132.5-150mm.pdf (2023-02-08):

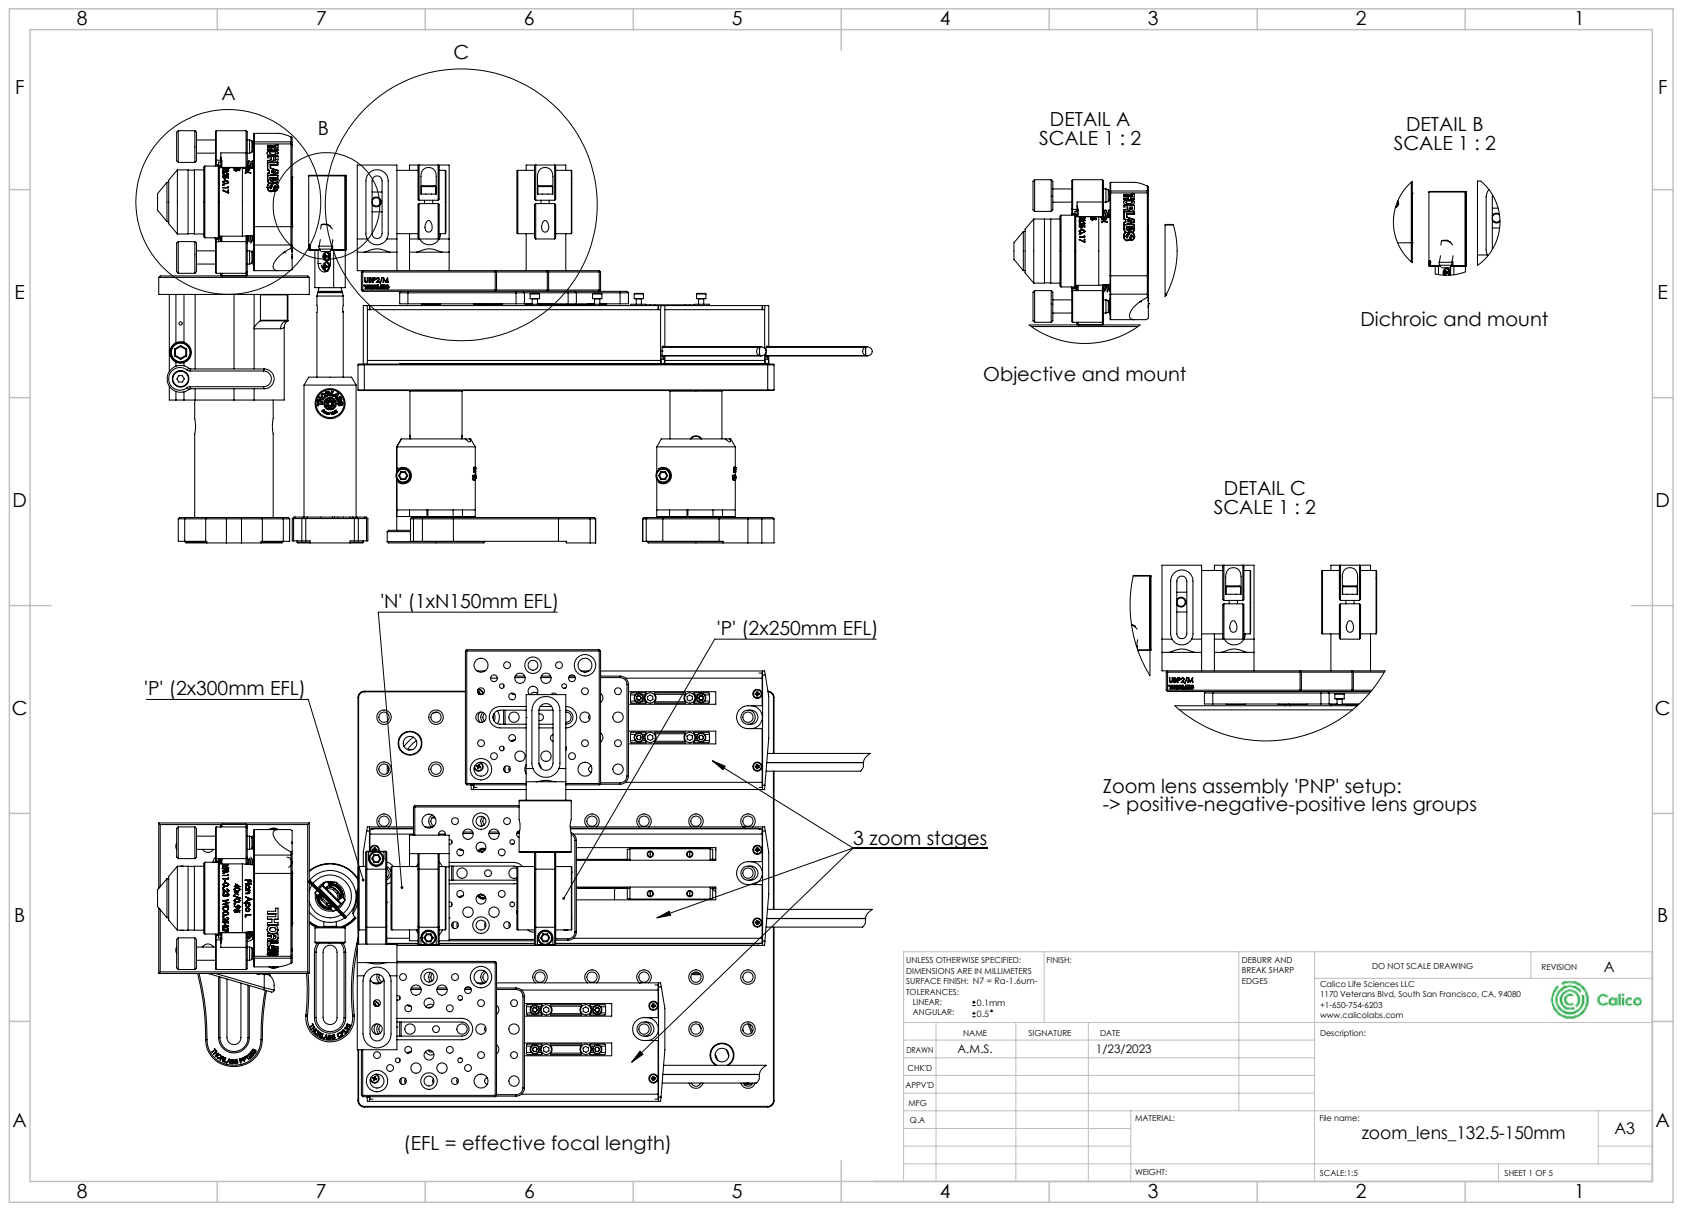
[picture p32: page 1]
'P' (2x300mm EFL); 'N' (1xN150mm EFL); 'P' (2x250mm EFL); 3 zoom stages; DETAIL A; SCALE 1 : 2; DETAIL B; DETAIL C SCALE 1 : 2; FINISH:; DEBURR AND; BREAK SHARP; DO NOT SCALE DRAWING; REVISION

Dichroic and mount

Objective and mount

Zoom lens assembly 'PNP' setup:
-> positive-negative-positive lens groups

UNLESS OTHERWISE SPECIFIED:
DIMENSIONS ARE IN MILLIMETERS
SURFACE FINISH:
TOLERANCES:
LINEAR:
ANGULAR:

Calico Life Sciences LLC
1170 Veterans Blvd, South San Francisco, CA, 94080
www.calicolabs.com

NAME | SIGNATURE | DATE | | Description:

DRAWN | A.M.S. | | 1/23/2023

CHK'D
APPV'D
MFG
Q.A | | | | MATERIAL: | File name: zoom_lens_132.5-150mm | A3

(EFL = effective focal length)

WEIGHT: | SCALE:1:5 | SHEET 1 OF 5

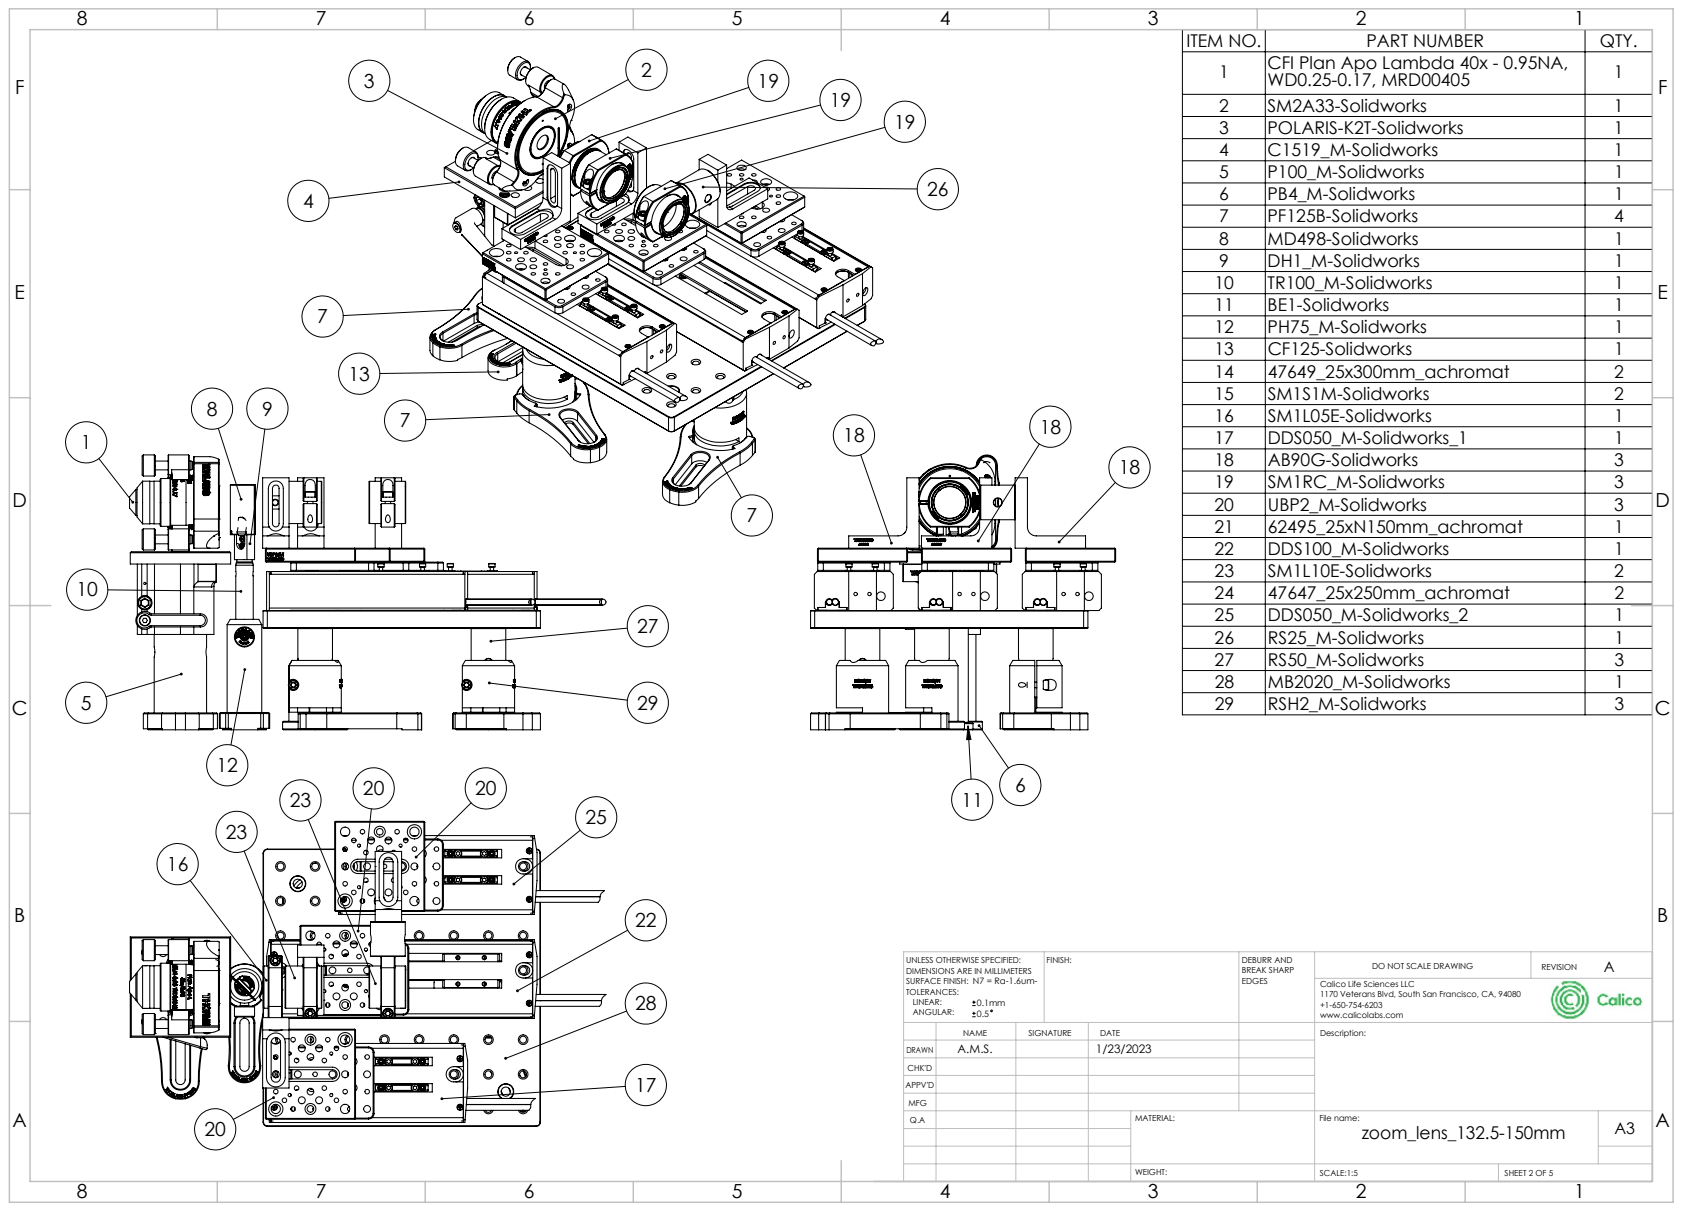
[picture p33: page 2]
FINISH:; DEBURR AND; BREAK SHARP; DO NOT SCALE DRAWING; REVISION

ITEM NO. | CFI Plan Apo Lambda 40x - 0.95NA, PART NUMBER | QTY. 1

WD0.25-0.17, MRD00405 | 1
2 | SM2A33-Solidworks | 1
3 | POLARIS-K2T-Solidworks | 1
4 | C1519_M-Solidworks | 1
5 | P100_M-Solidworks | 1
6 | PB4_M-Solidworks | 1
7 | PF125B-Solidworks | 4
8 | MD498-Solidworks | 1
9 | DH1_M-Solidworks | 1
10 | TR100_M-Solidworks | 1
11 | BE1-Solidworks | 1
12 | PH75_M-Solidworks | 1
13 | CF125-Solidworks | 1
14 | 47649_25x300mm_achromat | 2
15 | SM1S1M-Solidworks | 2
16 | SM1L05E-Solidworks | 1
17 | DDS050_M-Solidworks_1 | 1
18 | AB90G-Solidworks | 3
19 | SM1RC_M-Solidworks | 3
20 | UBP2_M-Solidworks | 3
21 | 62495_25xN150mm_achromat | 1
22 | DDS100_M-Solidworks | 1
23 | SM1L10E-Solidworks | 2
24 | 47647_25x250mm_achromat | 2
25 | DDS050_M-Solidworks_2 | 1
26 | RS25_M-Solidworks | 1
27 | RS50_M-Solidworks | 3
28 | MB2020_M-Solidworks | 1
29 | RSH2_M-Solidworks | 3

UNLESS OTHERWISE SPECIFIED:
DIMENSIONS ARE IN MILLIMETERS
SURFACE FINISH:
TOLERANCES:
LINEAR:
ANGULAR:

Calico Life Sciences LLC
1170 Veterans Blvd, South San Francisco, CA, 94080
www.calicolabs.com

NAME | SIGNATURE | DATE | Description:

DRAWN | A.M.S. | | 1/23/2023

CHK'D
APPV'D
MFG

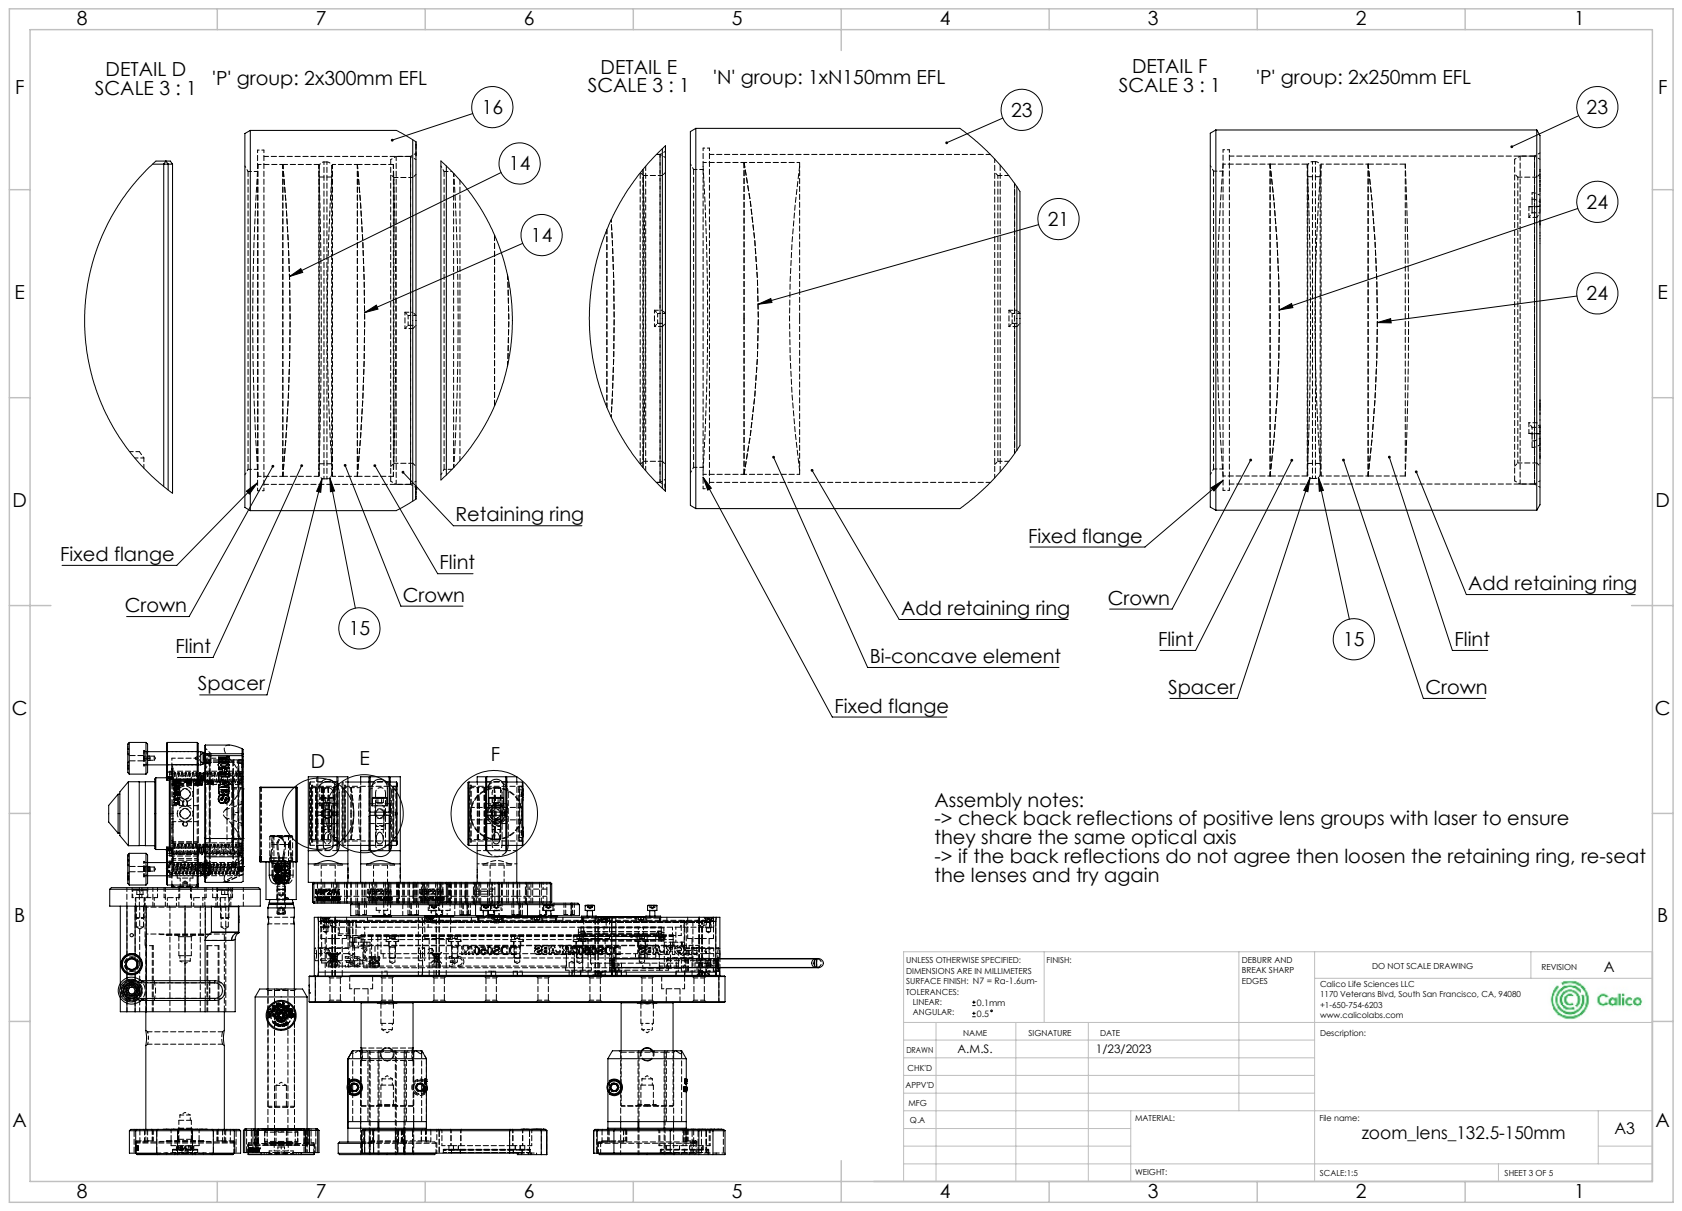
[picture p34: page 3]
DETAIL E SCALE 3 : 1; Fixed flange; Retaining ring; DETAIL F SCALE 3 : 1; 'N' group: 1xN150mm EFL; 'P' group: 2x250mm EFL; FINISH:; DEBURR AND; BREAK SHARP; DO NOT SCALE DRAWING; REVISION

DETAIL D
SCALE 3 : 1 'P' group: 2x300mm EFL

Add retaining ring

Bi-concave element
Fixed flange

Assembly notes:
-> check back reflections of positive lens groups with laser to ensure
they share the same optical axis
-> if the back reflections do not agree then loosen the retaining ring, re-seat
the lenses and try again

UNLESS OTHERWISE SPECIFIED:
DIMENSIONS ARE IN MILLIMETERS
SURFACE FINISH:
TOLERANCES:
LINEAR:
ANGULAR:

Calico Life Sciences LLC
1170 Veterans Blvd, South San Francisco, CA, 94080
www.calicolabs.com

NAME | SIGNATURE | DATE | Description:

DRAWN | A.M.S. | | 1/23/2023

CHK'D
APPV'D
MFG

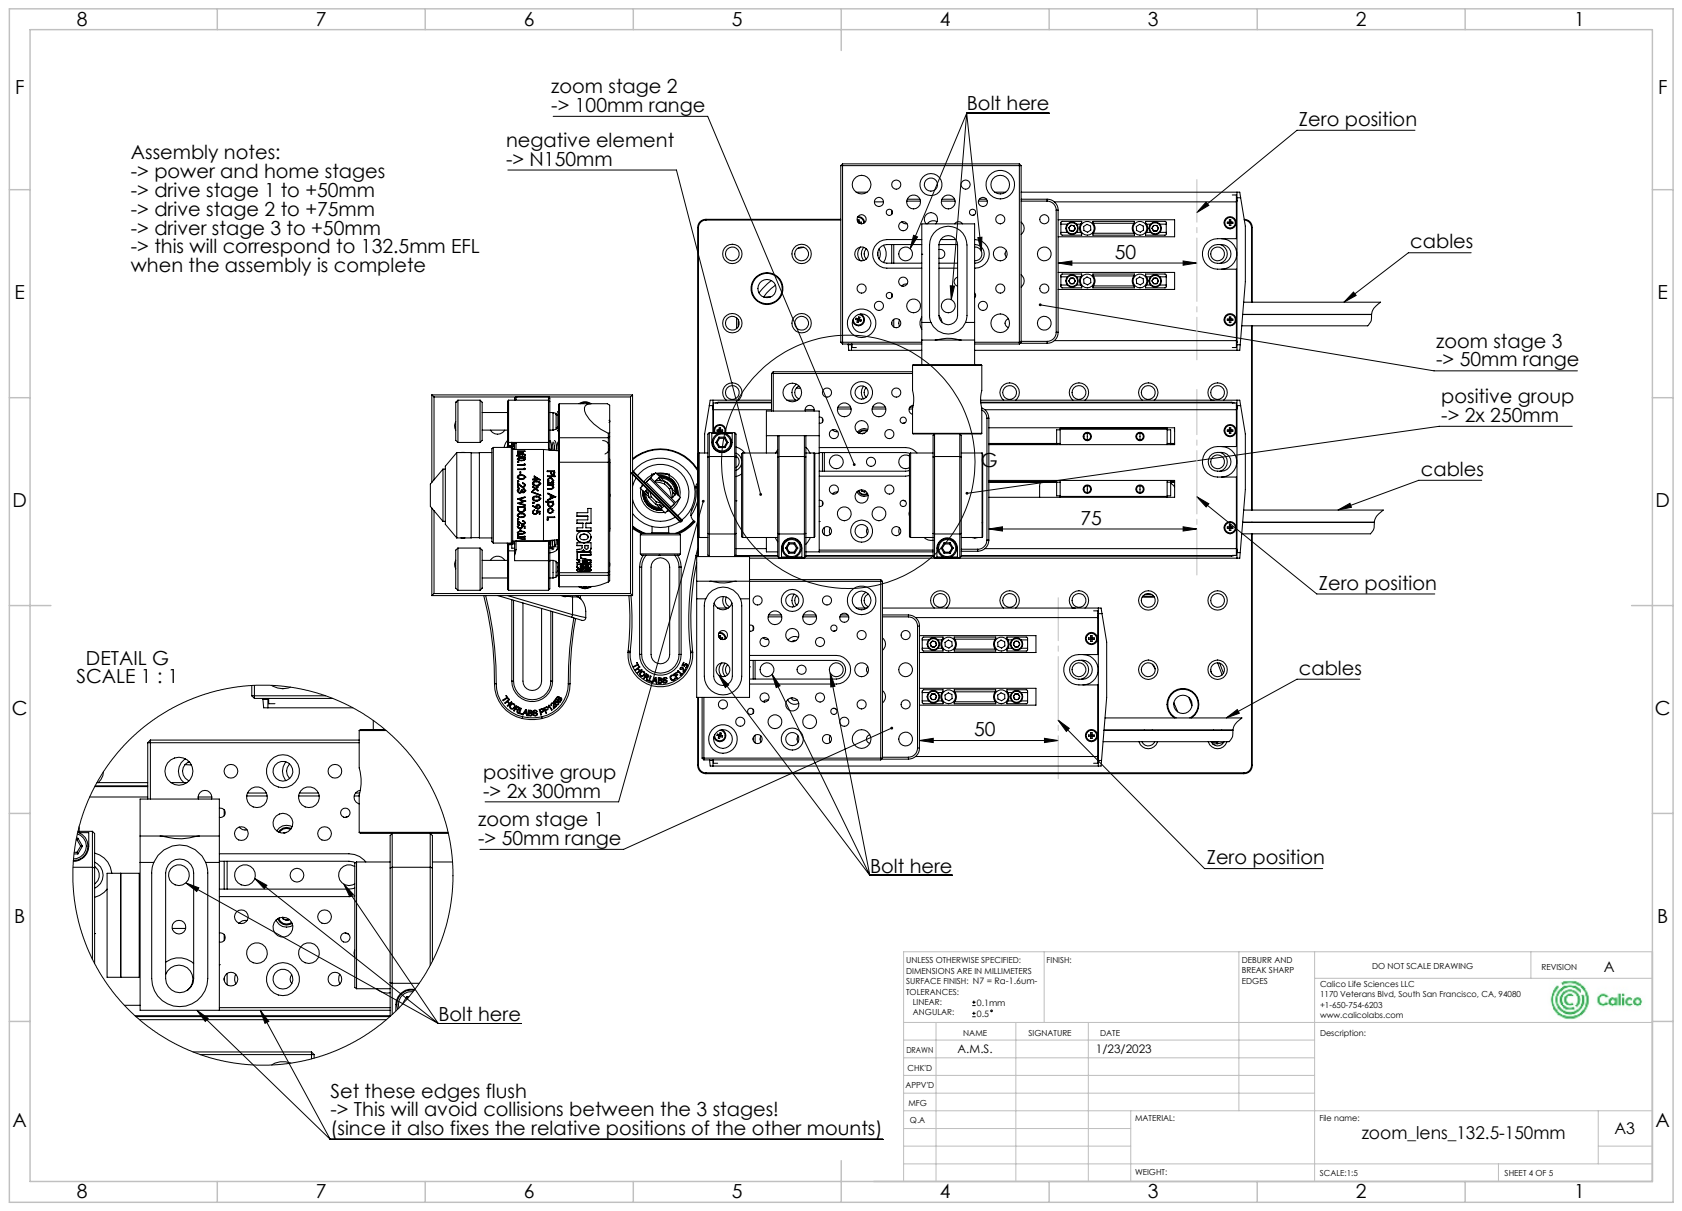
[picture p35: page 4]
negative element -> N150mm; positive group -> 2x 250mm; zoom stage 1 -> 50mm range; Zero position; positive group -> 2x 300mm; zoom stage 2 -> 100mm range; zoom stage 3 -> 50mm range; Bolt here; DETAIL G SCALE 1 : 1; FINISH:; DEBURR AND; BREAK SHARP; DO NOT SCALE DRAWING; REVISION

Assembly notes:
-> power and home stages
-> drive stage 1 to +50mm
-> drive stage 2 to +75mm
-> driver stage 3 to +50mm
-> this will correspond to 132.5mm EFL
when the assembly is complete

UNLESS OTHERWISE SPECIFIED:
DIMENSIONS ARE IN MILLIMETERS
SURFACE FINISH:
TOLERANCES:
LINEAR:
ANGULAR:

Calico Life Sciences LLC
1170 Veterans Blvd, South San Francisco, CA, 94080
www.calicolabs.com

NAME | SIGNATURE | DATE | Description:

DRAWN | A.M.S. | | 1/23/2023

CHK'D
APPV'D
MFG

Set these edges flush
-> This will avoid collisions between the 3 stages!
(since it also fixes the relative positions of the other mounts)

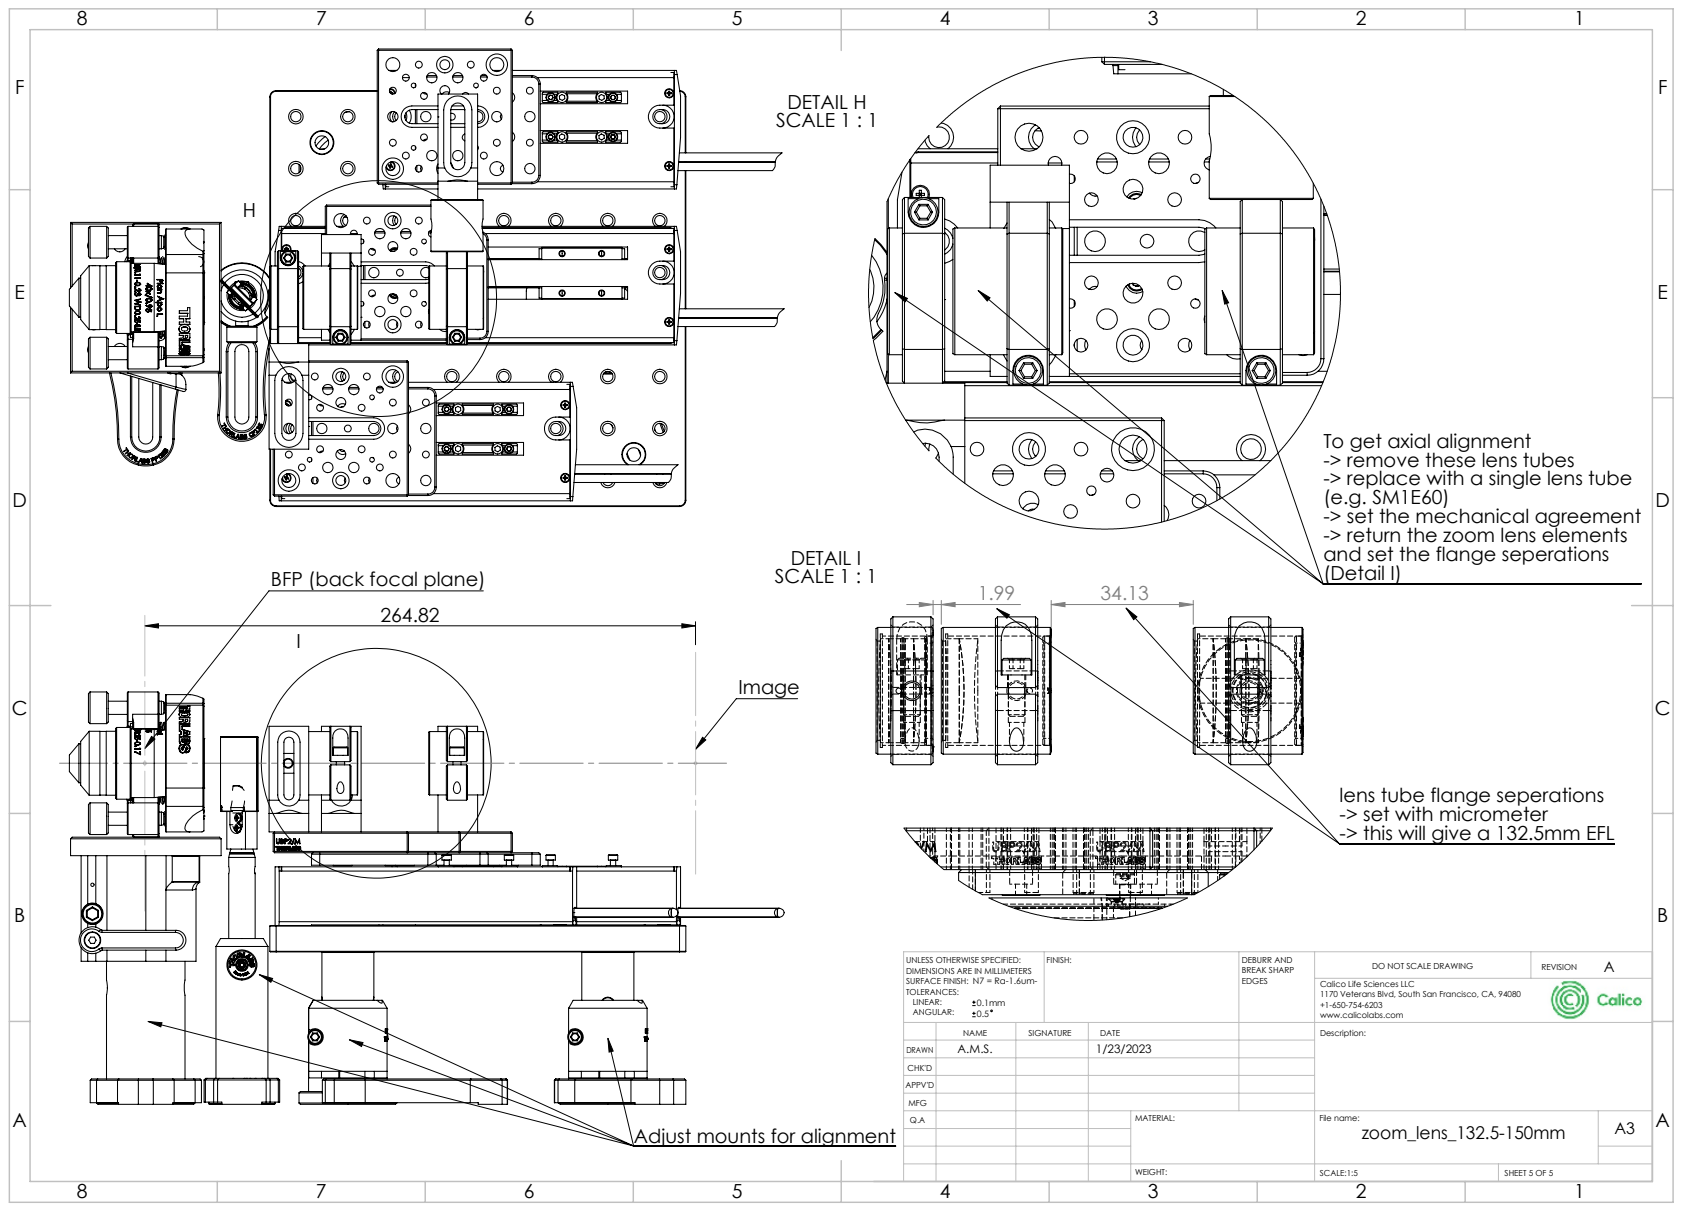
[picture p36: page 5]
DETAIL H SCALE 1 : 1; DETAIL I SCALE 1 : 1; FINISH:; DEBURR AND; BREAK SHARP; DO NOT SCALE DRAWING; REVISION

To get axial alignment
-> remove these lens tubes
-> replace with a single lens tube
-> set the mechanical agreement
-> return the zoom lens elements
and set the flange seperations
(Detail I)

BFP (back focal plane)

lens tube flange seperations
-> set with micrometer
-> this will give a 132.5mm EFL

UNLESS OTHERWISE SPECIFIED:
DIMENSIONS ARE IN MILLIMETERS
SURFACE FINISH:
TOLERANCES:
LINEAR:
ANGULAR:

Calico Life Sciences LLC
1170 Veterans Blvd, South San Francisco, CA, 94080
www.calicolabs.com

NAME | SIGNATURE | DATE | Description:

DRAWN | A.M.S. | | 1/23/2023

CHK'D
APPV'D
MFG

Adjust mounts for alignment

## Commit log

2022-07-07 Update index.html
    Zoom lens addition
2022-07-07 Update appendix.html
    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
2023-02-06 Add files via upload
    zoom lens mechanics update
2023-02-06 Add files via upload
    zoom lens optics update
2023-02-06 Update appendix.html
    zoom lens update
2023-02-15 Add files via upload
    Adding basic GUI for testing the zoom lens.
2023-03-23 Update index.html
    Adding a 'reversed' animation for the zoom lens showing the back focal plane (BFP)
2023-03-23 Add files via upload
    .pdf update for the newly added 'reversed' zoom lens animation.
2023-04-20 Update zoom_lens.py
    Added a new 'fast_init' option that uses threading to home the stages simultaneously. This takes about ~12s compared to about ~30s for the sequential home routine. For this to work the stages must be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
2023-10-05 Update zoom_lens_gui.py
    Minor update:
    - To simplify the 'main' block the tkinter 'root' is now nested in the 'init'.
    - Arguments for the stage COM ports have been added to ease switching between systems.
    - Improved function with 'verbose' and 'very_verbose' arguments.
    - Improved style with import details and 'return None' where appropriate.

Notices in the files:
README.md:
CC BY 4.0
